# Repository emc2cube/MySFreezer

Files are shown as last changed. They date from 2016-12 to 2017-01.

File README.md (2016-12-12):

MySFreezer
==========

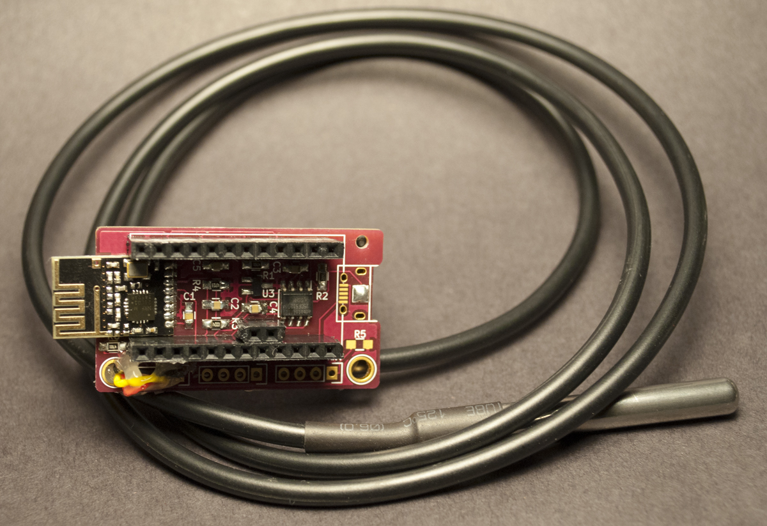
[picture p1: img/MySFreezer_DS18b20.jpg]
Node with DS18b20 probe

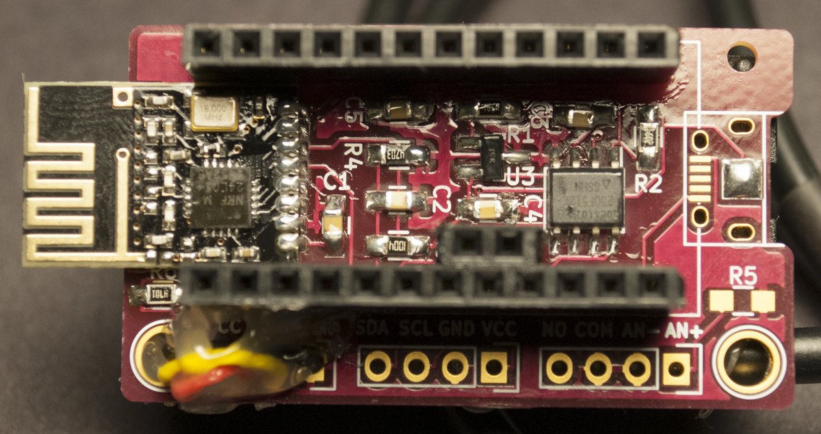
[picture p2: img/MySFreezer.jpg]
Node PCB detail

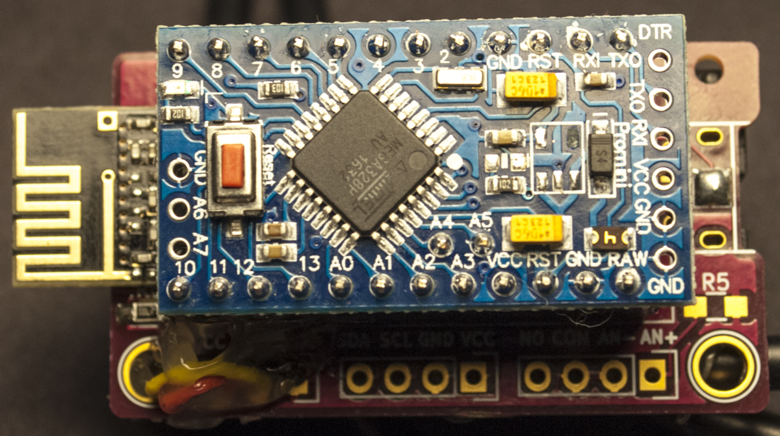
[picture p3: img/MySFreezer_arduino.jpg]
Node with Arduino

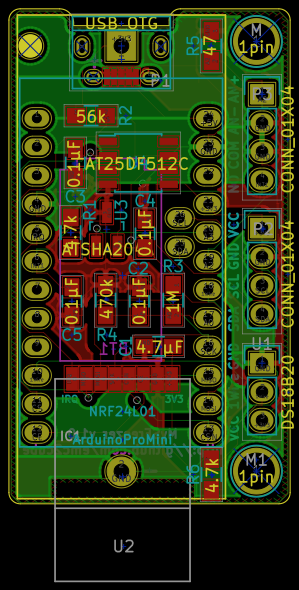
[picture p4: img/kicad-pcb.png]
KiCad view


Description
-----------

[MySensors](http://www.mysensors.org) sensor node aimed to monitor sensitive lab equipment, especially ultra low temperature -80°C freezers.

### 4-20mA sensor
4-20mA sensors are commonly available via a plug connector on the back of recent -80°C Freezer. This requires a 47Ω resistor in R5.
Connecting PCB "An-" and "An+" to a 4-20mA sensor will allow you to monitor your -80°C precisely without having to install anything inside the freezer.

### Alarm relay
Alarm relays are commonly available via a plug connector on the back of recent -80°C Freezer. They are also often present for industrial fridges, incubators, etc. Any of these can be monitored and will wake up the device when alarm is triggered.
Code is provided for Normally Open relays (circuit is closed when alarm is triggered) as they are the most commons, but a normally closed relay can also be used by updating the code.
Connecting PCB "NO" and "COM" to an alarm relay will allow you to monitor the alarm state of the device.

### I2C sensor
You can add extra I2C sensors if you need to expand the monitoring capacities of this PCB, or simply for extra versatility.
You will need to update the code to add support for your I2C sensor.
Exemple: add an Si7021 sensor and power the PCB via a USB wall charger and you can monitor a cold/hot room temperature and/or add a radio repeater.

### 1-Wire sensor / Thermistor probe
To monitor equipment lacking a 4-20mA output you can add a DS18b20 sensor on the 1-Wire port. This requires a 4.7kΩ resistor in R6.
Optionally by switching R6 to a higher value (ex: 10kΩ) you can update the code to use a thermistor probe by plugging it between "1Wire" and "GND"

Ordering
--------

Gerber files are included so you can order these PCB at your favorite PCB fab house and solder the few components yourself.
For an easy ordering process you can directly order these PCB without having to do anything else:
- [PCBs.io](https://PCBs.io/share/rNAbX) 4 for $6.78, black 1.2mm PCB, ENIG finish.
- [OSHPark.com](https://www.oshpark.com/shared_projects/mcg0E3wd) 3 for $8.55, purple 1.6mm PCB, ENIG finish.

Assembly
--------

If you plan to power this node by a battery it is advised to first prepare your arduino pro mini according to [MySensors battery powered sensors specifications](https://www.mysensors.org/build/battery) (removing Vreg and power indicator LED). You may also want to change your BOD fuse settings.
Do not remove the voltage regulator if you are powering the sensors using a USB wall charger, it will be used to power both arduino and radio module.

If you are using a battery holder start by soldering all SMD components except the radio module. Continue with arduino pin headers, trim them as close as you can of the PCB.
Then solder the battery holder and if you need trim the negative pin to be flush with the PCB. Finally you can carefully add the radio module.

Optional components
-------------------

### Resistors R5 and R6
- R5 is required if monitoring a 4-20mA sensor. For most accurate readings this resistor should be 47Ω with a <1% tolerance.
- R6 is only required if using a 1Wire Dallas sensor (4.7kΩ) or a thermistor probe (10kΩ or more depending on your thermistor)

### Capacitor C5
Only required while monitoring an Alarm relay. Prevents static noise to be detected as an alarm.

### Dual power mode
You can run this node using batteries, a CR123 battery holder can be mounted on the PCB, using + and - pins of the PCB.
It is also designed to use a micro USB connector as power input, any old USB phone charger will do.

### Battery monitoring
If using a battery to power the sensor current battery level can be sent to the controller if R3, R4 and C5 are installed.

### ATSHA204 module
For security reason you can add a CryptAuthEE SHA256 chip. This will allow you to sign messages and will secure communications between the node and your gateway (this is not encryption, just signing).
If you only control lights, fan, or other non-essential hardware you probably don't need to bother with this chip.
Signing can also be done at the software level, without the chip if you decide to add this function later.

### Eeprom module
This module is only used to perform OTA updates on the node. If you don't plan to use this feature you can also skip this chip.
You will also need to burn a compatible bootloader to your arduino (DualOptiBoot)

Arduino
-------

Included program(s)

### MySFreezerNode_4-20mA
Will monitor temperature using a 4-20mA sensor. This is calibrated for most of -80°C where 4ma equals -100°C and 20mA equals 50°C.
You can change this accordingly to your device specifications by updating the line "temperature = map(voltage, 225, 875, -100, 50);" in the code. While in MY_DEBUG mode you will also have access to the ADC level to perform a fine tuning.

### MySFreezerNode_DS18b20
Will monitor temperature using a DS18b20 temperature probe. If measured temperature is >-10°C then a software alarm will be activated. Temperature is defined by "TEMPERATURE_ALARM".

Revision history
----------------

Version 1.0: Initial release.

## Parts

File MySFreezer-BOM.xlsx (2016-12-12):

Quantity | Part | Value | Package | Manufacturer | Manufacturer P/N | Mouser P/N | Comment | Aliexpress or Ebay link
1 | P1 | USB_OTG | Micro USB connector | Hirose Connector | ZX62D-B-5PA8(30) | 798-ZX62D-B-5PA830 |  | https://www.aliexpress.com/item/Free-Shipping-100pcs-Micro-USB-5P-5-pin-Micro-USB-Jack-5Pins-Micro-USB-Connector-Tail/32307359968.html
1 | P2, P3 | CONN_01X04 | Pin Header Straight 1x04
1 | BT1 | Battery | CR123 battery holder | Keystone Electronics | 1051 | 534-1051 |  | https://www.aliexpress.com/item/CR123A-CR123-Lithium-Battery-Holder-Box-Clip-Case-w-PCB-Mounting-Lead-6Pcs/32739137115.html
1 | U1 | DS18B20 | Pin Header Straight 1x03
1 | U2 | NRF24L01 | NRF24L01-SMD radio module | Radio module | NRF24L01+ SMD
1 | U3 | ATSHA204A | SOT-23 | Atmel | ATSHA204A-STUCZ-T | 566-ATSHA204ASTUCZ-T | Optional, for signing
1 | U4 | AT25DF512C | SOIC-8 | Adesto Technologies | AT25DF512C-SSHN-B | 988-AT25DF512CSSHN-B | Optional, for OTA
1 | IC1 | ArduinoProMini | ArduinoProMini | Arduino Pro Mini 3.3V 8MHz | Arduino | Pro Mini 3.3V |  | https://www.aliexpress.com/item/10pcs-lot-Pro-Mini-328-Mini-3-3V-8M-ATMEGA328-ATMEGA328P-AU-3-3V-8MHz-for/1966734488.html
1 | C1 | 4.7µF | SMD 0805 | Murata | GRM21BR61C475KA88K | 81-GRM21BR61C475KA8K |  | http://www.aliexpress.com/item/1LOT-100PCS-Chip-Capacitors-4-7uF-475K-16V-10-0805-Package0805-2012-Metric/32561376020.html
4 | C2-C5 | 0.1µF | SMD 0805 | Murata | GRM21R71C104JA01D | 81-GRM21R71C104JA01D |  | http://www.aliexpress.com/item/1LOT-100PCS-Chip-Capacitors-0-1uF-104K-16V-10-0805-Package0805-2012-Metric/32560085454.html
2 | R1, R6 | 4.7k | SMD 0805 | Bourns | CR0805-JW-472ELF | 652-CR0805-JW-472ELF |  | http://www.aliexpress.com/item/100pcs-lot-SMD-Chip-Resistor-1-0805-4-7K-4700-OHMS-1-8W-100-YAGEO-New/32570155447.html
1 | R2 | 56k | SMD 0805 | Bourns | CR0805-JW-563ELF | 652-CR0805JW-563ELF |  | http://www.aliexpress.com/item/100pcs-lot-SMD-Chip-Resistor-1-0805-56K-1-8W-100-YAGEO-New-Original-Chip-Fixed/32570183133.html
1 | R3 | 1M | SMD 0805 | Bourns | CR0805-JW-105ELF | 652-CR0805JW-105ELF |  | https://www.aliexpress.com/item/100pcs-lot-SMD-Chip-Resistor-1-0805-1M-1-8W-100-YAGEO-New-Original-Chip-Fixed/32569356535.html
1 | R4 | 470k | SMD 0805 | Bourns | CR0805-JW-474ELF | 652-CR0805JW-474ELF |  | https://www.aliexpress.com/item/100pcs-lot-SMD-Chip-Resistor-1-0805-470K-1-8W-100-YAGEO-New-Original-Chip-Fixed/32569352634.html
1 | R5 | 47 | SMD 0805 | Susumu | RG2012N-470-W-T1 | 754-RG2012N-470-W-T1 | 0.05% tolerance

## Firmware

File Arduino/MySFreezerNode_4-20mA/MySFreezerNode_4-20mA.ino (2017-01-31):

/**
   The MySensors Arduino library handles the wireless radio link and protocol
   between your home built sensors/actuators and HA controller of choice.
   The sensors forms a self healing radio network with optional repeaters. Each
   repeater and gateway builds a routing tables in EEPROM which keeps track of the
   network topology allowing messages to be routed to nodes.

   Created by Henrik Ekblad <henrik.ekblad@mysensors.org>
   Copyright (C) 2013-2015 Sensnology AB
   Full contributor list: https://github.com/mysensors/Arduino/graphs/contributors

   Documentation: http://www.mysensors.org
   Support Forum: http://forum.mysensors.org

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
*/

// Customize your device name. You should use a pattern with 3 words separated by spaces "Room Nominal_Temperature Equipment"
// ex: "Lab -20°C Freezer" or "Hallway -80°C Freezer" or "TC 37°C Incubator".
String Location = "Lab -80°C Freezer";     // Location of the device, will be sent to the gateway with each device

// Enable debug prints
//#define MY_DEBUG

// Enable and select radio type attached
#define MY_RADIO_NRF24
//#define MY_RADIO_RFM69

#define ALARM_MONITORING_HW                 // Enable alarm monitoring using interrupt. Connect to COM (commmon) and NO (normally open) pins
//#define ALARM_MONITORING_SW                 // Enable software alarm, will be triggered by temperature
#define TEMPERATURE_ALARM -10               // If measured temperature is higher, alarm will activate. Required for ALARM_MONITORING_SW
#define TEMPERATURE_MONITORING              // Enable temperature monitoring, require one of the sensors to be activated
#define MA_SENSOR                           // Enable temperature monitoring using a 4-40ma output (usually available on -80ºC Freezers) using the An+ and An- ports
//#define DALLAS_SENSOR                       // Enable temperature monitoring using a DS18b20 probe. Use 3V3, 1Wire and GND ports
//#define THERMISTOR_SENSOR                   // Enable temperature monitoring using a thermistor probe. Thermistor should be wired between GND and the 1Wire ports.
#define BATTERY_MONITORING                  // Enable battery monitoring

// Set this to true if you want to send values altough the values did not change.
// This is only recommended when not running on batteries.
const bool SEND_ALWAYS = true;

#include <SPI.h>
#include <MySensors.h>

#if defined ALARM_MONITORING_HW
#define CHILD_ID_ALARM 0
#define ALARM_SENSOR 3                      // The digital input you attached your motion sensor.  (Only 2 and 3 generates interrupt!)
#define INTERRUPT ALARM_SENSOR-2            // Usually the interrupt = pin -2 (on uno/nano anyway)
MyMessage msgAlarm(CHILD_ID_ALARM, V_STATUS);
boolean alarm, lastAlarm;
#endif

#if defined ALARM_MONITORING_SW
#define CHILD_ID_ALARM 0
MyMessage msgAlarm(CHILD_ID_ALARM, V_STATUS);
boolean alarm, lastAlarm;
#endif

#if defined TEMPERATURE_MONITORING
#define CHILD_ID_TEMP 1
MyMessage msgTemp(CHILD_ID_TEMP, V_TEMP);
float temperature, lastTemp;

#if defined MA_SENSOR
#define MA_SENSOR_PIN A2                    // Analog pin for 4-20mA sensor, A2
#endif

#if defined DALLAS_SENSOR
#define ONE_WIRE_BUS 7                     // 1Wire pin, D7
#include <OneWire.h>
#include <DallasTemperature.h>
OneWire oneWire(ONE_WIRE_BUS);
DallasTemperature dallas(&oneWire);
int numSensors = 0;
#endif // end DALLAS_SENSOR

#if defined THERMISTOR_SENSOR
const int THERMISTOR_PIN = A1;              // Analog pin for thermistor, 1Wire pin, A1
#define THERMISTORNOMINAL 10000             // resistance at 25ºC
#define TEMPERATURENOMINAL 25               // temp. for nominal resistance (almost always 25ºC)
#define NUMSAMPLES 5                        // how many samples to take and average
#define BCOEFFICIENT 3950                   // The beta coefficient of the thermistor (usually 3000-4000)
#define SERIESRESISTOR 4700                 // We are using the 1Wire pullup 4.7kΩ as reference
int samples[NUMSAMPLES];
#endif // end THERMISTOR_SENSOR

#if defined MY_DEBUG
#define CHILD_ID_DEBUG 100
MyMessage msgDebug(CHILD_ID_DEBUG, V_CURRENT);
#endif // end TEMPERATURE_MONITORING + MY_DEBUG

#endif // end TEMPERATURE_MONITORING

#if defined BATTERY_MONITORING
const int  BATTERY_SENSE_PIN = A0;  // select the input pin for the battery sense point
int oldBatteryPcnt = 0;
#endif // end BATTERY_MONITORING

#define SN "MySFreezer"                     // Name of the sketch
#define SV "2.1.1"                          // Version (2.x : use MySensors 2.x)

#define MESSAGEWAIT 500                     // Wait a few ms between radio Tx

unsigned long SLEEP_TIME = 1800000UL;       // Sleep time between reads when alarm is off (in milliseconds)
unsigned long SLEEP_TIME_ALARM = 600000UL;  // Sleep time between reads when alarm is on (in milliseconds)
boolean metric = true;

void setup() {

#if defined DALLAS_SENSOR
  // Start up Dallas temperature probes
  dallas.begin();
  dallas.setWaitForConversion(false);
  numSensors = dallas.getDeviceCount();
#endif

#if defined MY_DEBUG
  // If debug, TX every 30s on idle / 10s on alarm
  SLEEP_TIME = 30000UL;                     // Sleep time between reads when alarm is off (30s)
  SLEEP_TIME_ALARM = 10000UL;               // Sleep time between reads when alarm is on (10s)
#endif

  metric = getControllerConfig().isMetric;  // was getConfig().isMetric; before MySensors v2.1.1

  // use the 1.1 V internal reference
#if defined(__AVR_ATmega2560__)
  analogReference(INTERNAL1V1);
#else
  analogReference(INTERNAL);
#endif

#if defined THERMISTOR_SENSOR
  pinMode(THERMISTOR_PIN, INPUT);
#endif
#if defined MA_SENSOR
  pinMode(MA_SENSOR_PIN, INPUT);
#endif
#if defined ALARM_MONITORING_HW
  pinMode(ALARM_SENSOR, INPUT_PULLUP);      // set the digital pin as input with internal pull-up resistor
#endif
  Serial.println(F("Node running"));
}

void presentation()
{
  // Send the Sketch Version Information to the Gateway
  wait(MESSAGEWAIT);
  sendSketchInfo(SN, SV);

  // Register all sensors to gw (they will be created as child devices)
#if (defined ALARM_MONITORING_HW || defined ALARM_MONITORING_SW)
  String alarmReg = Location + " Alarm";
  wait(MESSAGEWAIT);
  present(CHILD_ID_ALARM, S_BINARY, alarmReg.c_str());
#endif

#if defined TEMPERATURE_MONITORING
#if defined DALLAS_SENSOR
  numSensors = dallas.getDeviceCount();
  // Present all sensors to controller
  for (int i = CHILD_ID_TEMP; i < numSensors + CHILD_ID_TEMP; i++) {
    String dallasReg = Location + " Temp " + String(i - CHILD_ID_TEMP + 1);
    wait(MESSAGEWAIT);
    present(i, S_TEMP, dallasReg.c_str());
  }
#else
  String tempReg = Location + " Temp";
  wait(MESSAGEWAIT);
  present(CHILD_ID_TEMP, S_TEMP, tempReg.c_str());
#endif // end DALLAS_SENSOR
#if defined MY_DEBUG
  String debugReg = Location + " Debug";
  wait(MESSAGEWAIT);
  present(CHILD_ID_DEBUG, S_MULTIMETER, debugReg.c_str());
#endif // end TEMPERATURE_MONITORING + MY_DEBUG
#endif // end TEMPERATURE_MONITORING
}

void loop()
{

#if defined TEMPERATURE_MONITORING
  // Get temperature from various sensors
#if defined MA_SENSOR
  int voltage = analogRead(MA_SENSOR_PIN);
  wait(MESSAGEWAIT);
  voltage = analogRead(MA_SENSOR_PIN);
  temperature = map(voltage, 225, 875, -100, 50);
#if defined MY_DEBUG
  wait(MESSAGEWAIT);
  send(msgDebug.set(voltage, 0));
  Serial.print(F("Voltage ADC: "));
  Serial.println(voltage);
#endif
  if (SEND_ALWAYS || temperature != lastTemp) {
    lastTemp = temperature;
    if (!metric) {
      temperature = temperature * 9.0 / 5.0 + 32.0;
    }
    wait(MESSAGEWAIT);
    send(msgTemp.set(temperature, 1));
  }
#if defined MY_DEBUG
  Serial.print(F("Temperature: "));
  Serial.print(temperature);
  Serial.println(metric ? F(" °C") : F(" °F"));
#endif
#endif // end MA_SENSOR

#if defined DALLAS_SENSOR
#if defined MY_DEBUG
  Serial.print("Measuring  temperatures...");
#endif
  dallas.requestTemperatures(); // Send the command to get temperatures
#if defined MY_DEBUG
  Serial.println(" DONE");
#endif
  for (int i = 0; i < numSensors; i++) {
    // Fetch and round temperature to one decimal
    temperature = static_cast<float>(static_cast<int>((getConfig().isMetric ? dallas.getTempCByIndex(i) : dallas.getTempFByIndex(i)) * 10.)) / 10.;
    if (temperature != -127.00 && temperature != 85.00) {
      // Send in the new temperature
      if (SEND_ALWAYS || temperature != lastTemp) {
        lastTemp = temperature;
        wait(MESSAGEWAIT);
        send(msgTemp.setSensor(CHILD_ID_TEMP + i).set(temperature, 1));
      }
#if defined MY_DEBUG
      // After we got the temperatures, we can print them.
      // We use the function ByIndex, and as an example get the temperature from the first sensor only.
      Serial.print("Temperature for the device ");
      Serial.print(i);
      Serial.print(" is: ");
      Serial.print(temperature);
      Serial.println(getConfig().isMetric ? "C" : "F");
#endif
    }
  }
#endif // end DALLAS_SENSOR

#if defined THERMISTOR_SENSOR
  uint8_t i;
  float voltageR;
  for (i = 0; i < NUMSAMPLES; i++) {
    samples[i] = analogRead(THERMISTOR_PIN);
    wait(10);
  }
  // average all the samples out
  voltageR = 0;
  for (i = 0; i < NUMSAMPLES; i++) {
    voltageR += samples[i];
  }
  voltageR /= NUMSAMPLES;
#if defined MY_DEBUG
  wait(MESSAGEWAIT);
  send(msgDebug.set(voltageR, 0));
  Serial.print(F("Freezer voltage ADC: "));
  Serial.println(voltageR);
#endif
  temperature = (1 / ((log(voltageR / THERMISTORNOMINAL) / BCOEFFICIENT) + (1.0 / (TEMPERATURENOMINAL + 273.15)))) - 273.15;
  if (SEND_ALWAYS || temperature != lastTemp) {
    lastTemp = temperature;
    if (!metric) {
      temperature = temperature * 9.0 / 5.0 + 32.0;
    }
    wait(MESSAGEWAIT);
    send(msgTemp.set(temperature, 1));
  }
#if defined MY_DEBUG
  Serial.print(F("Temperature: "));
  Serial.print(temperature);
  Serial.println(metric ? F(" °C") : F(" °F"));
#endif
#endif // end THERMISTOR_SENSOR

#endif // end TEMPERATURE_MONITORING


#if (defined ALARM_MONITORING_HW || defined ALARM_MONITORING_SW)
#if defined ALARM_MONITORING_HW
  // Read alarm state
  boolean alarm = digitalRead(ALARM_SENSOR) == LOW;
#if defined MY_DEBUG
  Serial.print("Alarm: ");
  Serial.println(alarm ? "ON" : "OFF");
#endif
#endif
#if defined ALARM_MONITORING_SW
  // Define alarm state
  boolean alarm = temperature > TEMPERATURE_ALARM;
#if defined MY_DEBUG
  Serial.print("Alarm is ");
  Serial.print(alarm ? "ON ( " : "OFF ( ");
  Serial.print(temperature);
  Serial.print(getConfig().isMetric ? "C" : "F");
  Serial.print(alarm ? " > " : " ≤ ");
  Serial.print(TEMPERATURE_ALARM);
  Serial.println(getConfig().isMetric ? "C )" : "F )");
  Serial.println("");
#endif
#endif
  if (alarm != lastAlarm) {
    lastAlarm = alarm;
    wait(MESSAGEWAIT);
    send(msgAlarm.set(alarm ? "1" : "0")); // Send tripped value to gw
  }
#endif // end ALARM_MONITORING


#if defined BATTERY_MONITORING
  // get the battery Voltage
  int sensorValue = analogRead(BATTERY_SENSE_PIN);
  wait(MESSAGEWAIT);
  sensorValue = analogRead(BATTERY_SENSE_PIN);
#ifdef MY_DEBUG
  Serial.print(F("Battery voltage ADC: "));
  Serial.println(sensorValue);
#endif
  // 1M, 470K divider across battery and using internal ADC ref of 1.1V
  // Sense point is bypassed with 0.1 uF cap to reduce noise at that point
  // ((1e6+470e3)/470e3)*1.1 = Vmax = 3.44 Volts
  // 3.44/1023 = Volts per bit = 0.003363075
  int batteryPcnt = sensorValue / 10;
  batteryPcnt = batteryPcnt > 98 ? 100 : batteryPcnt;
#ifdef MY_DEBUG
  float batteryV  = sensorValue * 0.003363075;
  Serial.print("Battery voltage: ");
  Serial.print(batteryV);
  Serial.println(" V");
  Serial.print("Battery percent: ");
  Serial.print(batteryPcnt);
  Serial.println(" %");
#endif
  if (abs(batteryPcnt - oldBatteryPcnt) <= 1) {
    batteryPcnt = oldBatteryPcnt;
  }
  if (oldBatteryPcnt != batteryPcnt) {
    wait(MESSAGEWAIT);
    sendBatteryLevel(batteryPcnt);
    oldBatteryPcnt = batteryPcnt;
  }
#endif // end BATTERY_MONITORING
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

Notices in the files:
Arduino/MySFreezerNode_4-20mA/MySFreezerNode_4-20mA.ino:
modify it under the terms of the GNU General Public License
